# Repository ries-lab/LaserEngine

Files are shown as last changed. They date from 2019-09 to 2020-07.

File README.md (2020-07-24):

#  Open-source laser engine

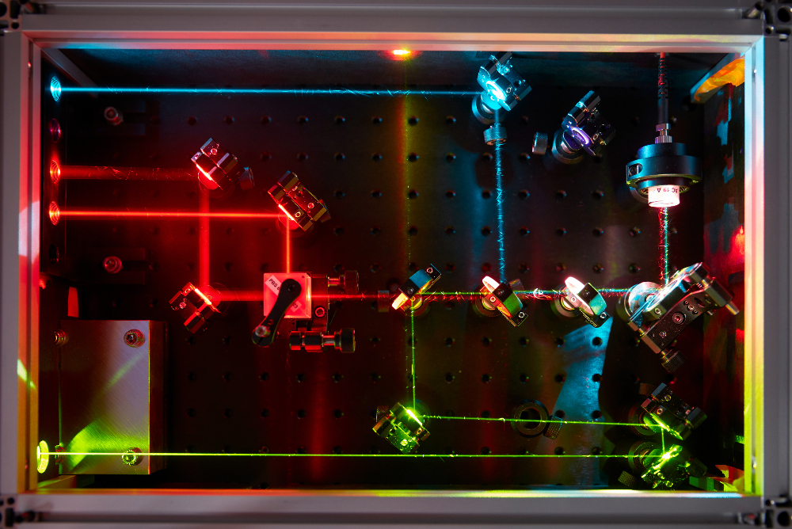
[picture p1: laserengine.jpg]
Laser engine


Blueprints for a low-cost laser engine compatible with wide-field and localization microscopy. The laser engine is based on affordable, albeit powerful, laser diodes, a square multimode fiber and a speckle-reduction module.

### :information_source: How to navigate the repository

The repository contains the following complementary modules:

- [Agitation module](Agitation_Module): a box holding a motor suspended by elastic cords for speckle and noise reduction.
- [Laser diode electronics](Electronics): Electronics to control the power and triggering of the laser diodes from the computer.
- [Laser engine](Laser_Engine): plans and guidelines of the optical path. It contains several submodules:
  - [Laser diodes mount](Laser_Engine/Diodes_Mount): A machined mount to host the TO56-canned laser diodes.
  - [Enclosure](Laser_Engine/Enclosure): A simple box to protect the laser engine from dust and the users from laser light.
  - [**(Optional)** Speckle-reduction for a 561 nm laser](Laser_Engine/LSR): In case of further speckle-reduction needed for a dpss laser, we present an optional element to place in the beam path.

### Repository updates

This repository is updated with the newest developments. If you wish to consult the repository in the state of the publication, please check out the tag **boe** within your local git copy:

```bash
git checkout boe
```

Or download the release [on Github](https://github.com/ries-lab/LaserEngine/releases/tag/boe) or [Zenodo](https://zenodo.org/badge/latestdoi/172924170).

###  :warning: Safety warnings :warning:

- Always work with adequate laser light protection.
- The foam board used in the [enclosure](Laser_Engine/Enclosure) is a fire hazard when subjected to strong laser light. Make sure to place beam stops behind the dichroic mirrors and the polarization beam splitter so that no laser beam hits the foam board panels. 
- Building the [electronics](Electronics) oneself requires experience in soldering and electronics in general. Make sure you are working safely.

#### Cite us

Daniel Schröder\*, Joran Deschamps\*, Anindita Dasgupta, Ulf Matti, and Jonas Ries, "Cost-efficient open source laser engine for microscopy," Biomed. Opt. Express 11, 609-623 (2020), [doi: 10.1364/BOE.380815](https://doi.org/10.1364/BOE.380815)

Repository on Zenodo:


#### Contact

If you have any question, get in touch with the [Ries group.](https://rieslab.de/#contact)

#### License 

[GNU LGPL](license.txt)

#### Acknowledgements

The electronics was designed by Christian Kieser, Electronics workshop, EMBL.

Pictures credit: *EMBL/Marietta Schupp*

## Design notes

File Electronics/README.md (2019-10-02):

## Electronics

To control the laser diodes, we imposed a set of constraints:

- Computer control of the **laser power** using a **[PWM](https://www.arduino.cc/en/tutorial/PWM) signal** ([Mojo FPGA](https://github.com/jdeschamps/MicroMojo) or Arduino).

- **Triggering of the laser diodes** (μs range) using a **TTL signal**.

- **Capping of the current** supplied to the laser diodes to avoid damages.

We present here two systems to drive the diodes: the electronics used in the manuscript and an alternative solution. Both are based on custom boards and commercial laser diode driver.

#### Current and voltage requirements

Note that different laser diodes have different voltage and current requirements, which complicates the task of finding a unique solution for all diodes of the laser engine:

| From the datasheets   | 405 nm, 80 mW <br />(dl-7146-301s, Sanyo) | 488 nm, 55 mW <br />(BLD-488-55, lasertack) | 640 nm, 700 mW <br />(HL63193MG, Oclaro) |
| --------------------- | ----------------------------------------- | ------------------------------------------- | ---------------------------------------- |
| Threshold current     | 60 mA                                     | 60 mA                                       | 250 mA                                   |
| Max operating current | 140 mA                                    | 135 mA                                      | 1000 mA                                  |
| Max operating voltage | 6 V                                       | 7.5 V                                       | 2.6 V                                    |

#### Solutions

We explored two solutions to control the laser diodes (we highlighted in bold each feature that is more advantageous in one version than in the other):

|                      |      [Electronics (manuscript)](Electronics_manuscript)      |     [Electronics (alternative)](Electronics_alternative)     |
| -------------------- | :----------------------------------------------------------: | :----------------------------------------------------------: |
| Status               |               **Daily use on our microscopes**               |                   Tested with a prototype                    |
| Inputs voltage       |                     3.3 V (PWM and TTL)                      |                **3.3 V or 5 V (PWM and TTL)**                |
| LD driver            | **4 x [EU-38-TTL](http://www.roithner-laser.com/ld_electronics.html) (total ~80 euros)** | 2 x [LD3000R](https://www.thorlabs.de/thorproduct.cfm?partnumber=LD3000R) + 2 x [LD1255R](https://www.thorlabs.de/thorproduct.cfm?partnumber=LD1255R) (total >600 euros) |
| Modified LD driver   |                             Yes                              |                            **No**                            |
| Power supplies       | **1 x [5 V (2.5 A)](https://www.reichelt.com/de/de/steckernetzteil-12-w-5-v-2-4-a-stabilisiert-gs15e-1p1j-p161604.html?&trstct=pos_0) + 1 x [6 V (1 A)](https://www.reichelt.com/de/en/eco-friendly-plug-in-power-supply-max-1000-ma-usb-mw-3k10gs-p87339.html?&trstct=pos_0)** | [See LD1255R power supply](https://www.thorlabs.de/newgrouppage9.cfm?objectgroup_id=1366) and <br />contact Thorlabs for the LD3000R |
| Power supplies price |                        ~ **24 euros**                        |                      prob. ~ 300 euros                       |
| Custom boards        | 4 x [signal conditioning](Electronics_manuscript/Custom_signal_conditioning) + 1 x [voltage distribution](Electronics_manuscript/Custom_voltage_distribution) |    **1 x [signal conditioning](Electronics_alternative)**    |
| LD pulsing           |                ~**40 μs (640) - 1 ms (488)**                 |                            few ms                            |

#### Notes:

- **Important**: The alternative electronics has only been tested **with a prototype**, while the manuscript version is used daily in our microscopes.
- In both cases, we generated the TTL and PWM signals using a Mojo FPGA. The FPGA firmware was based on the [MicroMojo project](https://github.com/jdeschamps/MicroMojo) and interfaced with the computer using [Micro-manager](https://micro-manager.org/). Alternatively, an Arduino can be used (also compatible with Micro-Manager).
- Each custom board was designed in [Altium](https://www.altium.com/); we uploaded here the Altium projects. Altium projects can be opened with a free license of the [Altium Designer Viewer](https://www.altium.com/altium-designer-viewer).
- The bill of materials for each custom board was exported in a format compatible with [Beta Layout](https://uk.beta-layout.com/pcb/) requirements. These can be used with the circuit PCB layout to order an already assembled board.

Both versions were designed by **Christian Kieser, Electronics workshop, EMBL**.

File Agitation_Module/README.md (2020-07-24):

## Agitation module

The agitation module consists of an aluminium box in which a motor is suspended by elastic cords. Turning on the motor causes strong vibrations in the elastics. By intertwining a multimode optical fiber in the elastics, the agitation module provides an efficient way to suppress speckles. 

#### Parts

###### Agitation box

- [Machined box parts](AgitationBox)
- [3D printed handle](AgitationBox/Handle) x1
- [Cable tie base](https://www.thorlabs.de/thorproduct.cfm?partnumber=CMS010) x4
- [2.5 mm elastic cords](https://www.prym.com/en/elastic-cord-1.5mm-black-3m-971064?c=4315) x3

###### Motor

- [Motor v1](Motors/Motor_v1) (used in the publication), which features a cheap [vibration electric motor](http://www.sourcingmap.com/dc-156v-16500rpm-vibration-electric-micro-mini-motor-140-for-massager-p-811318.html) with limited lifetime.
  or

- [Motor v2](Motors/Motor_v2) (newer version), which features a more expensive [brushless motor](https://www.amazon.de/gp/product/B07777ZH3J/ref=ox_sc_act_title_1?smid=A3TCAMEHRX2HS1&psc=1) with increased durability.

  **We advise using version v2 of the motor system.**

All non-machined or 3D-printed part references can be found in [the parts folder](Parts). Each motor version requires specific parts, described in their subfolders.

#### Guidelines

In the manuscript, we used an heavy aluminium box (30 cm thick walls):

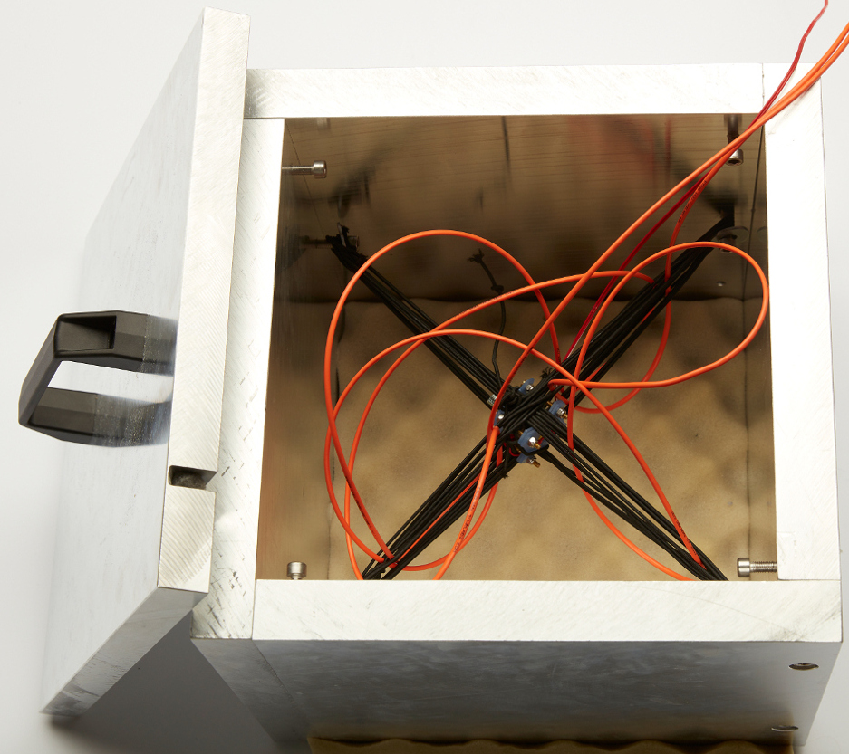
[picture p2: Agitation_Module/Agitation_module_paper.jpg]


Here, we present a lighter version:

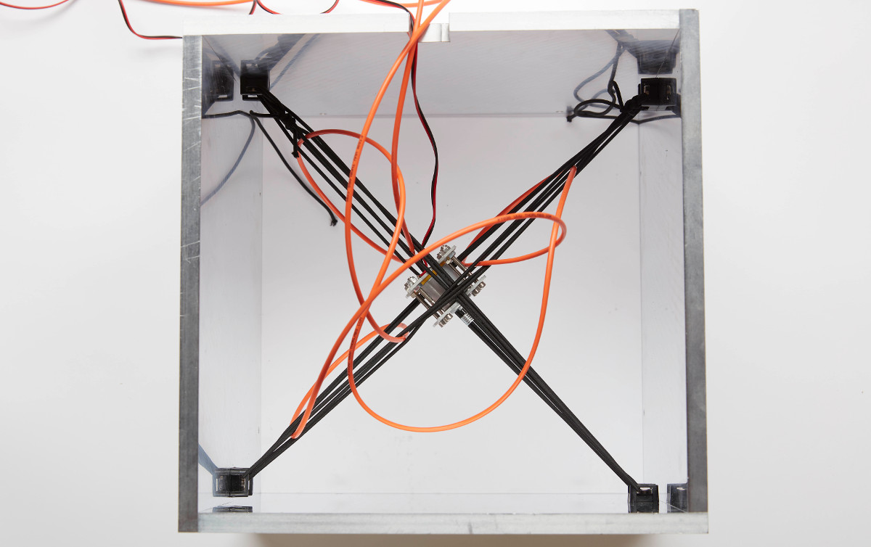
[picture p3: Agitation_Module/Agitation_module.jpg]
Agitation module


In their corresponding folders, you will find the guidelines regarding the mounting of the motor in its housing.

1. In [the box CAD folder](AgitationBox) you can find the blueprints for a lighter version of the agitation box. It consists of four panels screwed together with M4 screws. One of the panel has a dent to let the motor power supply cable and the optical fiber enter & leave the box. A lid is also described, with a [3D printed handle](AgitationBox_V2/Handle), in order to dampen the noise. The lid features four M3 screws at the corner to prevent it from sliding from the box.

   > Tip: We placed an egg box foam under the box to protect the floor and improve the noise dampening.

2. The box side panels each have an M4 thread to screw a cable tie base. The elastic cords can be tied to the handles of opposite base to create a diagonal bundle. **We advise creating a top and bottom bundles, along each diagonal, at least 5 cords strong each (as in the first picture).**

3. Mount the motor in its 3D-printed housing, either the [v1](Motors/Motor_v1) or the [v2](Motors/Motor_v2), according to its guidelines.

4. The v1 motor can simply be placed in between the elastic cord bundles, the bundles resting on a curved side of the housing (see pictures). The v2 motor can be secured to the elastic cord bundles with small cable ties going through its handles. 

5. In order to assert the efficiency of the speckle-reduction, image the optical fiber output on a camera (make sure you are focusing it properly) and turn on the motor. The speed of the motor (and therefore the supplied voltage), the tension of the cables and the mounting of the motor have an impact on the speckle-reduction efficiency.

Pictures credit: *EMBL/Marietta Schupp*

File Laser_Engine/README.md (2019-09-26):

## Laser engine optical path

The laser engine is composed of four submodules: the diode holder, the main optical path, the enclosure and the LSR system. The main optical path is described here, check the submodules for the corresponding part lists and guidelines.

#### Parts

- [405 nm laser diode (dl-7146-301s, Sanyo)](http://www.roithner-laser.com/ld_standard.html) x1

- [488 nm laser diode (BLD-488-55, Lasertack)](https://www.lasertack.com/en/55mw-488nm-laser-diode) x1

- [638 nm laser diodes (HL63193MG, Ushio)](https://www.lasershop.de/en/ushio-hl63193mg-red-laser-diode-700mw-5-6mm.html) x2

- [Diodes mount](Diodes_Mount)

- [Thorlabs part list](Parts/Thorlabs_parts_list)

- [Enclosure](Enclosure)

- [**(Optional)** 561 nm dpss laser](https://www.laserquantum.com/products/detail.cfm?id=65)

- [**(Optional)** LSR system](LSR)

#### Guidelines

The laser engine optical path is build on a breadboard, with each optical element centered on a hole to facilitate alignment:

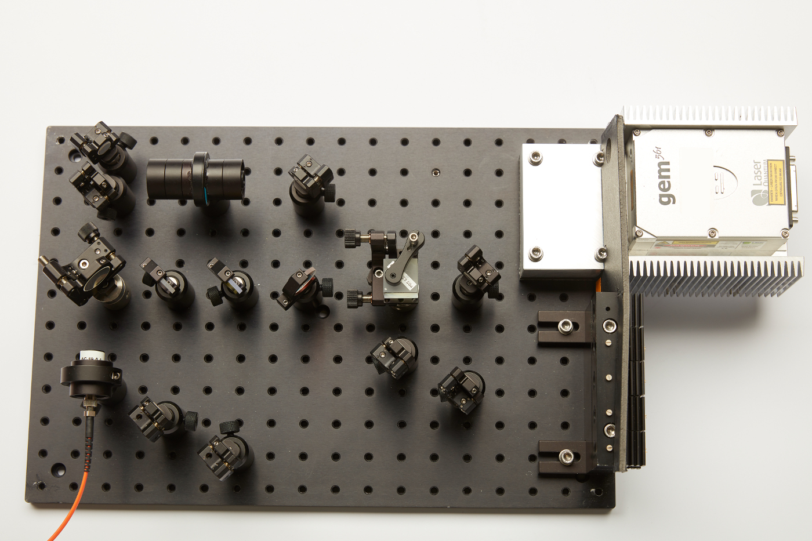
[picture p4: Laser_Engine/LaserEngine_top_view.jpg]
Optical path


The main optical path is composed of Thorlabs parts. Refer to [the following pdf](Optical_path_with_Thorlabs_parts.pdf) for the exact composition and position of each element (here in lower resolution):

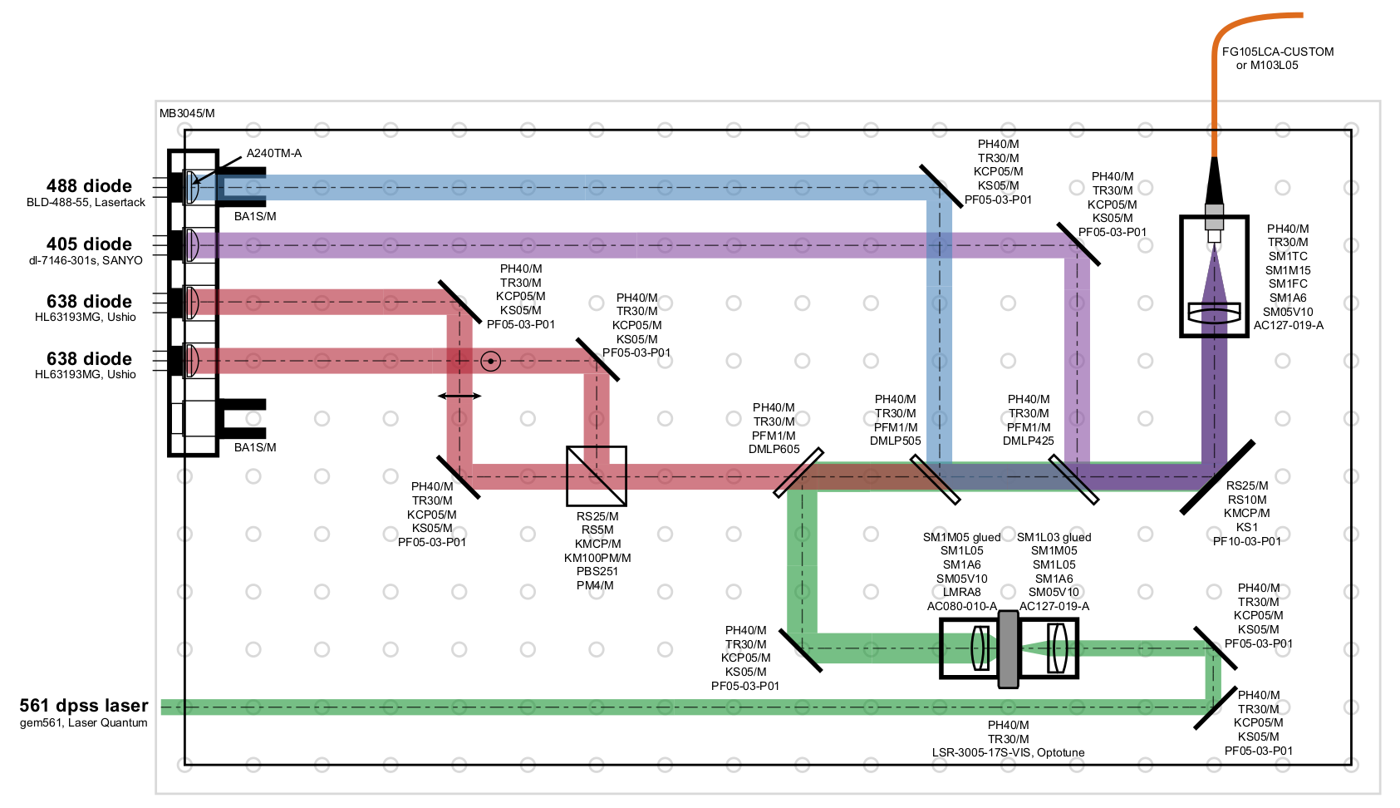
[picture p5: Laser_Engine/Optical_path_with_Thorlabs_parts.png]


Note that the LSR system is only needed if you need further speckle reduction with a dpss laser. The alignment procedure for the LSR system can be found [here](LSR). The LSR system is composed of all elements of the beam path that are exclusively on the 561 nm laser path.

> **Important**: The laser diode and dpss laser can be quite bright and will be collimated during alignment, **wear appropriate laser light protection**.

1. The first step is to mount the diodes in the holder and collimate them (see [diodes mount](Diodes_Mount)).
2. Place and fix the mount on the breadboard (use the picture above as reference for the positioning) so that the back is aligned with the edge. The collimated beams from each diode should go along the breadboard holes.
3. The easiest way to align the coupling system (multimode fiber and lens) is to couple an alignment laser from the optical fiber exit (with respect to the laser engine) and collimate the output. Place the fiber adapter plate at the extremity of the SM1M15 lens tube. The lens tube can then be held by a SM1 clamp (SM1TC) mounted on the post. Then mount the 19 mm lens in the 1/2" adjustable lens tube (SM05V10) and place the lens tube on the SM05-SM1 adapter.  At the other extremity of the SM1M15, screw the adapter with the lens residing inside the lens tube (SM1M15). You can then move the lens inward by screwing further the SM05V10 on the adapter. Once the laser light collimated, fix the SM05V10 with the locking ring.
4. Use the collimated laser coming from the optical fiber to fix the coupling system at the right height (**70 mm**) and angle (laser along the holes of the breadboard).
5. Place the reflective elements (mirrors, dichroics, beam splitter) at the positions indicated [on the optical path plan](Optical_path_with_Thorlabs_parts.pdf). Use the collimated laser to set the heights and angle (laser going along the holes).
6. Remove the alignment laser and place a power meter at the fiber exit in order to report the laser power coming out of the optical fiber. Each laser beam has two mirrors (or one mirror and one dichroic mirror) allowing to walk the beam. Start by aligning the shortest wavelength (here the 405 nm diode): first walk the beam until some laser light exits the fiber, then maximize the power coming out.
7. Repeat for the 488 nm diode. 
8. If present, align the 561 nm laser. If applicable, refer to the [laser speckle reducer](LSR) module in order to mount the LSR correctly. Coupling of the laser in the optical fiber is better achieved with the LSR turned on (as the coupling efficiency might be different with or without the LSR running).
9. The two red laser diodes are superimposed using perpendicular polarizations and a polarization beam splitter. In order to align the polarizations, place the polarization beam splitter in the right orientation (refer to the [Thorlabs page](https://www.thorlabs.de/newgrouppage9.cfm?objectgroup_id=739) for the cube orientation). Then slightly unscrew the heat sink on the first red diode. If the diode beam is the transmitted one, then rotate the diode until its profile is horizontal (you need to be above the lasing threshold). Maximize the transmitted power through the beam splitter before fixing again the diode on the mount.
10. Next, repeat the procedure with the second laser diode, with this time a perpendicular orientation of the beam profile. (If the laser beam is the reflected beam, then the profile should be oriented vertically).
11. Finally, maximize the coupling of the red diodes in the optical fiber by beam walking them. Coupling can further be improved by also rotating the square optical fiber so that the long axis of the fiber profile is aligned with the long axis of the diode profiles. 
12. Place the enclosure on top of the breadboard to protect the user and the optics. 
    **:warning: Warning: make sure to place beam stops to prevent strong laser light from hitting the foam board, as it can catch fire. :warning:**
13. The illumination on the microscope is described in the paper and might depends on the microscope itself.

We obtained the following coupling efficiencies (these might vary):

| with square optical fiber (M103L05) | Coupling efficiency |
| ----------------------------------- | :-----------------: |
| 405 nm                              |         47%         |
| 488 nm                              |         80%         |
| 638-1 nm                            |         80%         |
| 638-2 nm                            |         80%         |
| 561 nm (LSR)                        |         50%         |
| 561 nm (no LSR)                     |         81%         |

> Note that the fiber launch might also have an impact on the illumination profile and that playing with the coupling in of the laser beam can lead to a better profile (more top-hat) albeit with a lower coupling efficiency. 

Pictures credit: *EMBL/Marietta Schupp*

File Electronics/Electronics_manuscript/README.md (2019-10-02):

## Electronics (manuscript)

This section describes the electronics used in the paper. Here, the electronics is based on an inexpensive laser diode driver and was packaged in a control box.

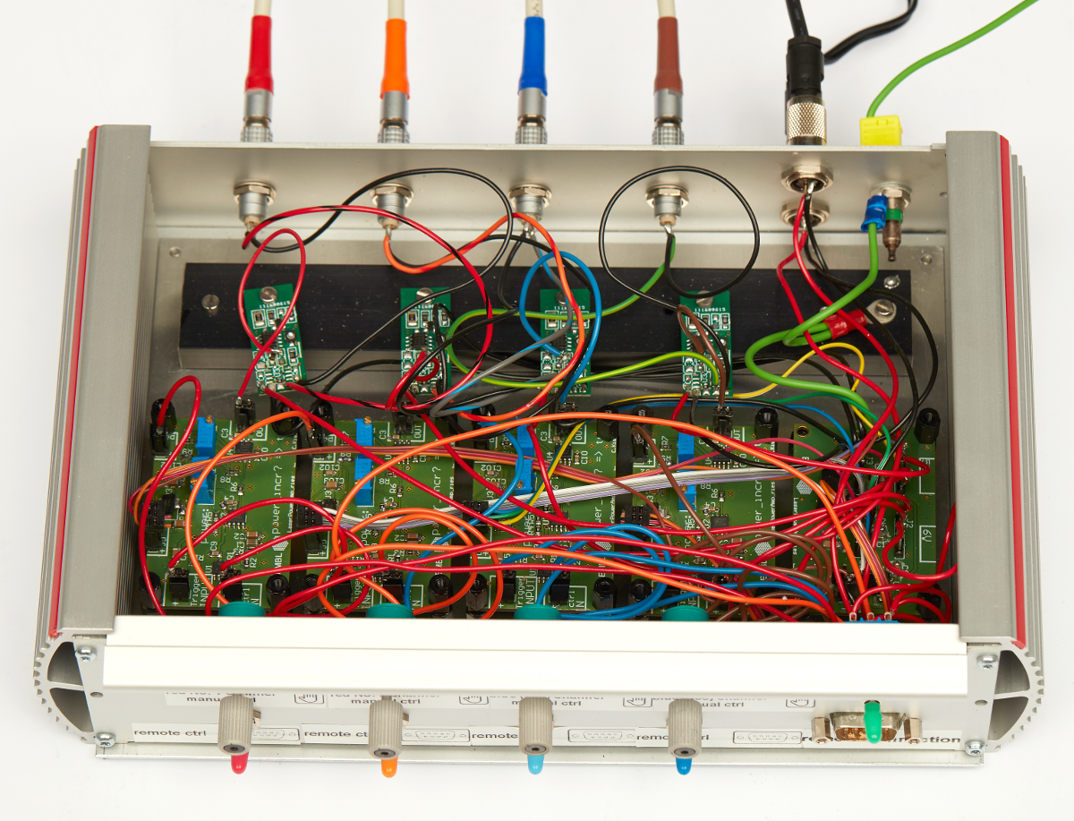
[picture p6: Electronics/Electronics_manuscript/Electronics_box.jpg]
Electronics box


The commercial **laser diode drivers** can be seen on the top row of the picture. They have been modified to bypass the board potentiometer with the output of the **signal conditioning board** (bottom row). There is one laser diode driver and one voltage conditioning board per laser diode. Finally, a **voltage distribution board** (bottom right) provides the correct voltage to each of the other elements.

The electronics has two inputs per laser diode:

- 3.3 V TTL trigger signal to switch on or off the diodes
- 3.3 V PWM (>= 1kHz) signal

**This section does not describe the boxing out of the electronics. You can find a description of the wiring involved in the [wiring](Wiring) submodule.** In particular, a feature of our electronics box is a main switch to turn on/off the laser diode and switches to allow for individual manual or remote control of the laser diodes.

#### Parts

For the four diodes described in [this section](https://github.com/ries-lab/LaserEngine/tree/master/Electronics), we need:

- [Laser diode driver](http://www.roithner-laser.com/ld_electronics.html) (eu-38-ttl, Roithner) x4

- Heat sink for the laser diode drivers (see picture above)

- [Signal conditioning board A](Custom_signal_conditioning) x2

- [Signal conditioning board B](Custom_signal_conditioning) x2

- [Voltage distribution board](Custom_voltage_distribution) x1

- [Power supply #1](https://www.reichelt.com/de/en/eco-friendly-plug-in-power-supply-max-1000-ma-usb-mw-3k10gs-p87339.html?&trstct=pos_0) (set to 6 V, 1 A)

- [Power supply #2](https://www.reichelt.com/de/de/steckernetzteil-12-w-5-v-2-4-a-stabilisiert-gs15e-1p1j-p161604.html?&trstct=pos_0) (5 V, 2.5 A)

- Controller (Arduino Due or [Mojo FPGA](https://github.com/jdeschamps/MicroMojo)) capable of delivering 3.3 V TTLs and PWMs signals 

#### Guidelines

 The guidelines describe few steps we took to build the electronics. For each laser diode, theses steps were followed independently. We advise repeating these steps in case of laser diode to laser diode variability. If you order the custom boards with the components already soldered, they you might want to verify the first steps to insure you have the correct current range output. The grounds from all boards and power supplies are connected.

> **Important**: **The laser diodes need to have proper heat dissipation otherwise they will not reach their maximum output power and will shut off, or even be irremediably damaged.** 

1. In all further steps, the voltage supply originates from the [voltage distribution board](Custom_voltage_distribution). Check the corresponding submodule for the guidelines relative to the voltage supply wiring.

   > Note: In our case, the laser diode drivers for the 405 nm and 488 nm required 5 V, while the drivers for the 638 nm laser diodes required 6 V.

2. **Connect the commercial laser diode driver to the laser diode without powering it**. Respect the anode / cathode pins. **Decrease the potentiometer to the minimum (measure the output current)**.

3. Slowly increase the laser diode output power using the potentiometer and measure the voltage between the two resistors (see picture). Measure the voltage at the maximum power output (Vmax): 

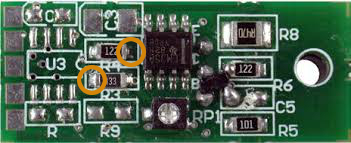
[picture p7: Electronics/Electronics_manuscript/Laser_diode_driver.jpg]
eu-38-ttl
   |  |
   | :----------------------------------: |
   | Copyright Roithner LaserTechnik GmbH |

   For instance, we obtained:

| 405 nm  | 488 nm  | 638 nm (1) | 638 nm (2) |
| ------- | ------- | ---------- | ---------- |
| 40 mV | 40 mV | 330 mV    | 330 mV    |

   Measure in addition the **maximum current** going to the laser diode.

4. Then, **[calculate](http://www.ohmslawcalculator.com/voltage-divider-calculator)** the resistors needed in the voltage divider part of the signal conversion board. As we wanted to scale the voltage from 0 - 3.3 V to 0 - Vmax. In our case, this yields two different **signal conditioning boards (A and B)** with different voltage division factors (see **[circuit](Custom_signal_conditioning/Circuit)** for the positions of the resistors R1, R2 and R3):

   |                         | A: 405 / 488 nm | B: 638 nm |
   | ----------------------- | --------------- | --------- |
   | Voltage division factor | 79              | 10        |
   | Z1 (R1 + R2)            | 68 + 10 kΩ      | 0 + 9 kΩ  |
   | Z2 (R3)                 | 1 kΩ            | 1 kΩ      |

   > Note: The voltage divider circuit is followed by an amplification and offset stages on the circuit. The choice of the voltage division dictates the range of current that can be supplied to the laser diode driver. Choosing a lower voltage after division would allow for the possibility to decrease in the future the maximum voltage supplied without exchanging the resistors.

5. **Once the resistors soldered on the signal conditioning board**, the output voltage (Out signal) range needs to be tuned using the two **potentiometers (#1 and #2, respectively R10 and R12 on the [circuit](Custom_signal_conditioning/Circuit))** present on the board. **Connect the PWM (3.3 V, we used a period of 2 ms) source to the signal conditioning board**.

6. In an iterative manner, turn potentiometer #1 (offset) so the minimum of the PWM signal corresponds to a slightly negative voltage (few mV). Then tune potentiometer #2 (gain) so that the maximum of the PWM corresponds to expected maximum output voltage. Repeat until the minimum is few mV negative and the maximum the expected value measured in step 2.

   > Note that if you did not reach the correct range, the voltage divider factor will have to be modified to increase or decrease it (by choosing different resistors).

7. The next step requires modifying the commercial laser diode driver and connecting it to the signal conditioning board. Unsolder the resistors on the laser diode driver at the points where the voltage was measured previously. **Pull the unsoldered pins away from the board and solder them together with the positive output from the signal conditioning board**.

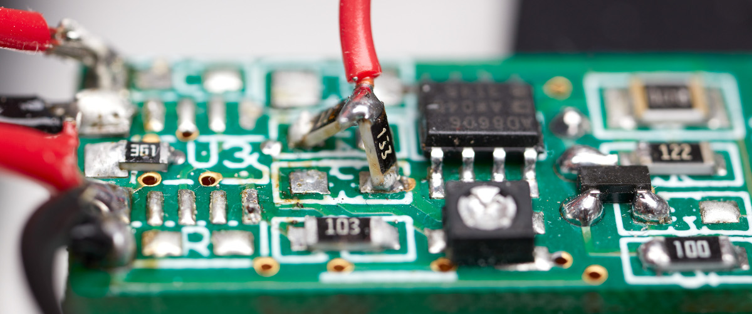
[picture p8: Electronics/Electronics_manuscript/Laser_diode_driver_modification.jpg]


   > **Note from Roithner Lasertechnik GmbH**: Any modification to the EU-38-TTL is carried out at ones own risk and responsibility. Roithner Lasertechnik GmbH has not verified and can not be held liable for any operating failure or damage resulting from the modification to the driver.

8. Before connecting back the laser diode, verify that the current output of the laser diode driver is still close to the measured current in step 2.

9. If the laser diode is still emitting at the minimum PWM value, decrease slightly potentiometer #1.

10. Repeat for the other laser diodes. Then wire the TTL inputs directly on the laser diode drivers.

#### Pulsing lag and rise-time

Using an oscilloscope, we measured the delay, the rise time and the fall time of each diode while using a TTL trigger with a pulse length of 4 ms (405 nm and 488 nm) or 400 μs (638 nm). Note that the results depend on the power set-point (separated by a "|").

| PWM 33% \| 100% |      405 nm      |     488 nm     |    638 nm (1)    |   638 nm (2)    |
| --------------- | :--------------: | :------------: | :--------------: | :-------------: |
| Delay           | 400 μs \| 400 μs | 1 ms \| 700 μs |  40 μs \| 2 μs   |  60 μs \| 5 μs  |
| Rise time       | 100 μs \| 77 μs  | 157 μs\| 67 μs |  18 μs \| 13 μs  | 15 μs \| 21 μs  |
| Fall time       |  26 μs \| 1 μs   | 15 μs \| 7 μs  | 300 μs \| 500 ns | 170 ns\| 600 ns |

#### Possible improvement

- Remove the 3.3 voltage generation in the signal conditioning boards and instead make it available through the voltage distribution board.
- Redesigned the voltage distribution board to take only the 5 V power supply and generate the 6 V voltage by itself.

Close-up picture of the modified laser diode driver credit: *EMBL/Marietta Schupp*

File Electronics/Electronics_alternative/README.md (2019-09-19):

## Electronics (alternative)

#### **Important: the electronics described here was validated using a prototype only.**

The electronics introduced in this section is an alternative to the electronics used on our microscopes and in the manuscript. It should more easily reproducible as it does not involve modifying the laser diode drivers and uses only a single custom board. However, the laser diode drivers and the power supplies are substantially more expensive. 

- **Input** (per laser diode): a TTL signal (3.3 V or 5 V) for triggering and a PWM signal (3.3 V or 5 V) for laser power control.
- **Triggering with ms pulses**.
- **Capping of the current to the laser diodes to avoid damage**.

#### Parts

For the four diodes described in [this section](https://github.com/ries-lab/LaserEngine/tree/master/Electronics).

- [High current driver LD3000R](https://www.thorlabs.de/thorproduct.cfm?partnumber=LD3000R) x2

- Power supply for the LD3000R: Note that the LD300R requires positive as well as a negative voltage power supplies. Contact Thorlabs for guidelines on choosing an appropriate power source.

- [Low current driver LD1255R](https://www.thorlabs.de/thorproduct.cfm?partnumber=LD1255R) x2

- [Power supply for the LD1255R + cable](https://www.thorlabs.de/newgrouppage9.cfm?objectgroup_id=1366) x2

- [Custom laser diode signal conversion board](Custom_signal_conditioning) x1

- Power supply for the custom board (12 V) x1

- Controller (Arduino or Mojo FPGA) capable of delivering 3.3 V or 5 V TTLs and PWMs signals. 

#### Guidelines

The laser diodes used in this project require two different current range: 60-150 mA (405 nm and 488 nm LDs) and 100-1000 mA (638 nm LDs). Therefore they are controlled here by two different LD drivers:

|                    | 405 nm & 488 nm                                              | 638 nm                                                       |
| ------------------ | ------------------------------------------------------------ | ------------------------------------------------------------ |
| Laser diode driver | [LD1255R](https://www.thorlabs.de/thorproduct.cfm?partnumber=LD1255R) | [LD3000R](https://www.thorlabs.de/thorproduct.cfm?partnumber=LD3000R) |

Each LD driver can be set to an external control mode by placing a jumper on two pins (J2). Refer to their respective data sheet and set them to external control mode.

The [custom signal conversion board](Custom_signal_conditioning) takes two inputs (3.3 V or 5 V):

- TTL trigger for on/off switching and pulsing
- PWM for power control

The board features five channels (for five laser diodes) that can be adapted to the input type and voltage. Each channel has a header:

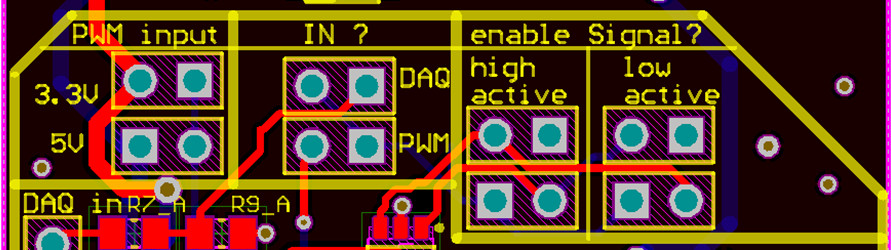
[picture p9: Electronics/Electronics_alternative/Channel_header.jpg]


Using jumpers, choose for each channel:

- 3.3 V or 5 V input
- Analog or PWM input for power control
- High or Low active for the trigger

**Important: place only a single jumper in each section (the yellow rectangles on the picture)! Note that for the high or low active, there are two sections, therefore two jumpers are necessary (top and bottom).**

The signal conversion board produces an analog signal that can be fed directly onto the external control pin of the LD drivers. **In addition, it features a potentiometer that allows decreasing the maximum voltage fed to the LD driver (< 5 V) in order to cap the current at the laser diode and prevent damages.**

Finally, make sure to correctly wire the anode and the cathode of each diode to the proper pin on the LD drivers.

> **Note**: The last segment of the circuit (see [circuit](Custom_signal_conditioning/Circuit)) holds two resistors R5 and R6 which are open and 0 Ω respectively. Therefore this part of the circuit is just a voltage follower. However, replacing R5 and R6 would allow for higher output voltage if ever necessary (e.g. 0-10V). 
>
> **Note**: We did not attempt to supply the positive and negative voltages for the LD3000R, LD1255R and the custom board using the same sources. It should be possible to reduce the number of power supply by grouping them.

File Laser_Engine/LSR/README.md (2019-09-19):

## Laser speckle-reducer assembly (optional)

The LSR system is aimed at further suppressing the laser speckles present in the output of a mutimode fiber-coupled 561 diode-pumped solid state laser. It is based on the LSR-3005-17S-VIS from Optotune, which features an oscillating membrane with diffusers. **We advise starting without this system and adding it only if the residual speckles are shown to be much stronger than those of the laser diodes.**

> Note that the LSR limits exposure times to >5 ms. 

#### Parts

Note that the Thorlabs parts used here are already present in the [Thorlabs cart corresponding to the laser engine with LSR system](https://github.com/ries-lab/LaserEngine/tree/master/Laser_Engine/Parts/Thorlabs_parts_list).

- [LSR-3005-17S-VIS, Optotune](https://www.optotune.com/products/laser-speckle-reducers/eap-lsr/lsr-3005-series) x1

- [gem561 laser](https://www.laserquantum.com/products/detail.cfm?id=65) x1

- UV glue

#### Guidelines

In order to obtain high quality speckle-reduction, the laser light must be focused on the LSR oscillating membrane and then collimated for fiber-coupling. Here, we describe the mounting and alignment of the lenses on the LSR (picture on the left).

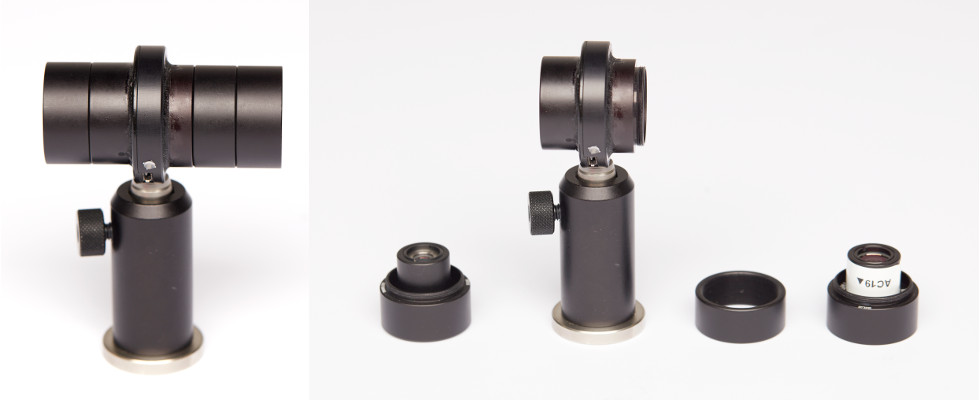
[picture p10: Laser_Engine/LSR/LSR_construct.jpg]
LSR construct


We will call the side of the LSR with prints (and a countersink hole) the "exit" and the back-side the "entrance". 

1. Make sure that the 561 nm laser is collimated before aligning the LSR system and that it propagates along the holes on the table, according to [this schematic](https://github.com/ries-lab/LaserEngine/blob/master/Laser_Engine/Optical_path_with_Thorlabs_parts.pdf).

2. Glue the 10 mm lens on its lens adapter.

3. Place each lens, the 10 mm and the 19 mm, within a SM05V10 1/2" lens tube.

4. Lock a SM1A6 1/2" to 1" adapter close to the non-threaded side of two SM1L05 lens tube.

5. Insert the SM05V10 holding the lenses each within one of the 1/2" to 1" adapter (see left-most and right-most elements on the picture on the right above). The lenses should stick out on the threaded side of the lens tubes.

6. Glue a SM1M05 on the exit side of the LSR using UV glue. Do the same with a SM1L03 on the entrance side (thread pointing outward). They should be as centered as possible, in particular with respect to each other (they should be on the same axis). See the picture above (left).

7. Screw the LSR with post and post-holder (the post holder should be a standard post holder, as opposed to the pedestal post holder on the above picture) in position in the laser engine beam path.

8. Screw a SM1M05 on the entrance side of the LSR and the element including the 19 mm lens on the same SM1M05. 

9. **With the LSR turned off**, you should see speckles in the laser bream profile after the LSR. Move the lens inward or outward in order to maximize the size of the speckles in the profile. Once you find a position with large speckles, lock the SM05V10 in place using a lock ring.

   > **Note**: The "maximum size" of the speckles is somewhat subjective, look for the larger speckles in the profile and estimate a position where they seem bigger.

10. Unscrew the entrance elements and rotate the LSR 180 degrees on its base.

11. Repeat the procedure with the 10 mm lens until you maximize the speckles size.

12. Finally, rotate again the LSR and put back the lens tube system on the entrance side . Move the laser so that the beam goes again along the holes if it has moved.

13. Place the last mirror before the dichroic (see schematic).

Pictures credit: *EMBL/Marietta Schupp*

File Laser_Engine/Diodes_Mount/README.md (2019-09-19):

## Diodes mount

The diodes mount holds all four TO56-canned laser diodes and allows for efficient heat dissipation. The mount also contain the collimating lens and can be easily fixed on the laser engine breadboard.

#### Parts

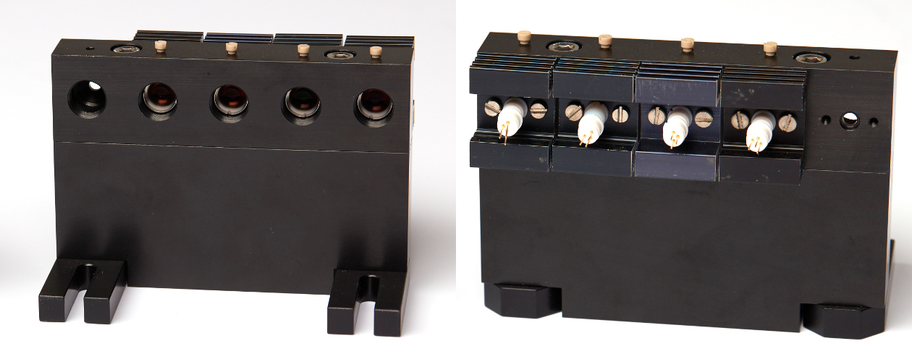
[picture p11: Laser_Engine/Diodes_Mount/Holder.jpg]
Mount


- Laser diodes (see [the main optical path section](https://github.com/ries-lab/LaserEngine/tree/master/Laser_Engine))

- [Machined mount](Machined_Mount) x1

- BA1S/M base x2

- [Heat sinks with custom holes](Heat_sinks) x4

  > **Note**: The heat sinks were produced from a longer heat sink (SK 75 75, fischer elektronik). Each heat sink was cut to be 24 mm long in order to fit more easily side by side. 25 mm long heat sinks (SK 75 25, fisher elektronik) should also work.

- Thermal paste

- [Diode sockets](https://www.buerklin.com/de/Produkte/Aktive-Bauelemente/Zubeh%C3%B6r-f%C3%BCr-Halbleiter/Halbleiterfassungen/HALBL-FASSG-TF183/p/12B190) x4

- M2 plastic screws (> 13 mm) x4

- A240TM-A aspheric lens x4

  All non-machined part references can be found in [the parts folder](Parts). **Note that the BA1S/M and the lenses are present in the [Thorlabs part list](https://github.com/ries-lab/LaserEngine/tree/master/Laser_Engine/Parts/Thorlabs_parts_list)**.

#### Guidelines

> **Note**: Laser diodes are sensitive to electrostatic discharges. If possible, use grounding when working with unmounted laser diodes.

1. Assemble the [laser diode mount](Machined_Mount) using long M6 screws. Then, with shorter ones, add the BA1S/M feet the mount base.
2. Apply a small amount of thermal paste on the sides of each laser diode (on the area where it is in contact with the mount). Then place the laser diodes in their aperture, center it and fix it by screwing on a heat sink. **Make sure that none of the laser diode pins are in contact with the heat sink to avoid shorting.** Test the diodes.
3. In order to collimate the diodes, first roughly screw the aspheric lenses in. Then turn on the diode you are collimating to a voltage above the lasing threshold (when the center linear profile starts becoming bright). **Make sure you are wearing proper laser light protections.**
4. Move the lens in or out until the laser central spot profile is not changing much during propagation over several meters. 
5. Fix the lens using the plastic screws. Avoid excessive tightening so as to not break the screw.
6. Repeat for all diodes, then move on to the laser engine alignment.

Pictures credit: *EMBL/Marietta Schupp*

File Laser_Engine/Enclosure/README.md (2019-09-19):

## Enclosure

The enclosure serves two purposes: protect the users from laser light and prevent dust from depositing on the optics. 

#### Parts

- [Aluminium profiles (25.01.####, mk)](Posts)

- [Foamboard panels (LKG55070, Boesner)](Foamboard_panels)

- [Tension fasteners](https://shop.mk-group.com/verbindungselemente/spannverbindungen/296/spannverbinder-serie-25) x8

- Tension plug (see mk catalog, 25.50.3321, mk) x4

- 3 mm M6 square nuts and 16 mm M6 maggot screws (x4)

  > **Note**: The mk 25 profiles can be bought directly from the company. An alternative to the mk 25 system is sold by [Thorlabs](https://www.thorlabs.de/newgrouppage9.cfm?objectgroup_id=194).

The components are also referenced in the [part list](Parts).

#### Guidelines

#### :warning: The foam board is sensitive to laser light and can catch fire, place beam stop to prevent string laser light from hitting the panels. :warning:

The enclosure consists of a mk 25 aluminium profile system and foamboard panels (LKG55070, Boesner) :

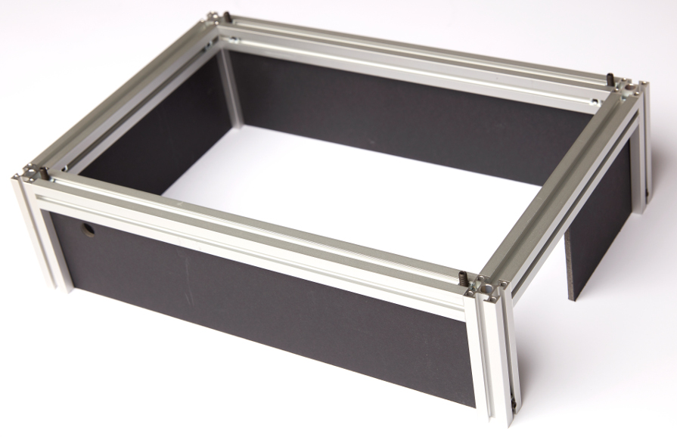
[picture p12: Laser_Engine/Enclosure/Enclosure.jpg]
Enclosure


The aluminium profiles drawing can be found in the following [folder](Posts). In order to build the enclosure, 8 MK25 aluminium profiles are necessary: 4x 120 mm long (vertical pillars), 2x 250 mm long (short side) and 2x 400 mm long (long side). 

> **Note**: All horizontal pillars have two holes on the same face to accommodate the tension fasteners (B51.03.009, mk). The fastener principle is explained in the following [catalogue](https://www.mk-group.com/fileadmin/media/catalog/en/mk_Profile_Technology_4.0.pdf), page 104. The vertical pillars have a single hole allowing locking a tension plug (25.50.3321, mk) in a similar manner.

The horizontal profiles are fixed to the vertical pillars using the tension fasteners (B51.03.009, mk). Next, we used four [foamboard panels](Foamboard_panels) inserted in the rim of the vertical pillars as side panels for the enclosure. Note that we did not draw the hole for the 561 nm laser, as this might depends on the laser itself and its mounting principle.

Four additional M6 square nuts (3 mm thick), each wtih a M6 maggot screw (16 mm long), were inserted in the top rim of the horizontal long-side pillars. The M6 screws therefore stick out of the horizontal pillar rims (see picture) and correspond to the four holes in the foamboard lid. Place the nuts correctly, then tighten the maggot screws to lock the nut in position.

Finally, we placed four mk tension plug (25.50.3321, see mk catalogue) on the laser engine breadboard corner M6 thread. The heads of the tension plugs fits in the central column of the vertical pillars and can be secured with a square nut and screw as before (see the base of the vertical pillars on the right side of the picture).

As in the picture above, the side panels have cut-out corresponding to specific elements of the laser engine: a circular hole to allow the optical fiber to enter the laser engine, a cut-out of the diode mount size and a circular hole for the 561 nm laser (optional, not drawn/represented here).  

Pictures credit: *EMBL/Marietta Schupp*

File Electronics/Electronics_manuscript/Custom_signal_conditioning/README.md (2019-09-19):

## Signal conditioning board

We produced two versions of the voltage conditioning board (A and B) with different voltage divider circuits, corresponding either the 405 nm and 488 nm (A) or the 638 nm (B)  laser diodes.

The custom board was designed using Altium (the project can be viewed with a free license of the [Altium Designer Viewer](https://www.altium.com/altium-designer-viewer)). You can find the project [here](Altium_project).

A [bill of materials](Bill_of_materials) and a [schematic of the circuit](Circuit) were automatically generated with Altium.

##### Power supply

The power is supplied to the signal conditioning board by the [custom voltage distribution board](https://github.com/ries-lab/LaserEngine/tree/master/Electronics/Electronics_manuscript/Custom_voltage_distribution): +5 V, gnd and -5 V.

##### Inputs

- 3.3 V TTL trigger signal
- 3.3 V (>=1 kHz) PWM control signal (to set the power of the laser diode)

##### Output

- Out: the Out signal should be fed directly at the intersection of the two resistors on the modified EU-38-TTL (see [previous section](https://github.com/ries-lab/LaserEngine/tree/master/Electronics/Electronics_manuscript)).
- 3.3 V voltage supply: can be used with a potentiometer to generate a manual control signal (see the [wiring](https://github.com/ries-lab/LaserEngine/tree/master/Electronics/Electronics_manuscript/Wiring) submodule for how we used a switch and a potentiometer for manual power control).

> Note: see [the wiring section](https://github.com/ries-lab/LaserEngine/tree/master/Electronics/Electronics_manuscript/Wiring) for more details on how we wired the custom boards in the electronics box.

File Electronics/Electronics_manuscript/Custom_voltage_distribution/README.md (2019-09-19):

## Voltage distribution board

The voltage distribution board simplifies the wiring within our electronics box and allows delivering negative voltage to the signal conditioning board without having a negative power supply.

#### Parts

Note that we worked with two power supplies:

- [Power supply #1](https://www.reichelt.com/de/en/eco-friendly-plug-in-power-supply-max-1000-ma-usb-mw-3k10gs-p87339.html?&trstct=pos_0) (set to 6 V, 1 A)

- [Power supply #2](https://www.reichelt.com/de/de/steckernetzteil-12-w-5-v-2-4-a-stabilisiert-gs15e-1p1j-p161604.html?&trstct=pos_0) (5 V, 2.5 A)

#### Guidelines

In order to supply voltage to the laser diode driver and to the signal conditioning board:

1. Wire the power supplies ground to the ground on the voltage distribution board.

2. Set power supply #1 voltage to 6 V. Wire its positive pin to the +6 V area of the board.

3. Wire power supply #2 positive pin to the +5 V area of the board.

   > Note: We actually soldered an interrupter between the power supplies positive pin and the voltage distribution board to be able to turn off the circuit. See the [wiring section](https://github.com/ries-lab/LaserEngine/tree/master/Electronics/Electronics_manuscript/Wiring) for more details.

4. The signal conditioning boards have 3 pins for the voltage supply: -5 V, GND and +5 V. Wire them accordingly using pins from the -5 V, ground and +5 V areas on the voltage distribution board.

5. The laser diode driver require different voltage, depending on the diodes they power. Wire the ground to the ground area, then the positive signal from the following voltage area on the board:

   | 405 nm & 488 nm | 638 nm (x2) |
   | :-------------: | :---------: |
   |      +5 V       |    +6 V     |

> Note: see [the wiring section](https://github.com/ries-lab/LaserEngine/tree/master/Electronics/Electronics_manuscript/Wiring) for more details on how we wired the custom boards in the electronics box.

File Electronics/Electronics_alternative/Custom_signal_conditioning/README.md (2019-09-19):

## Signal conditioning board

The custom board was designed using Altium (the project can be viewed with a free license of the [Altium Designer Viewer](https://www.altium.com/altium-designer-viewer)). You can find the project [here](Altium_project).

A [bill of materials](Bill_of_materials) and a [schematic of the circuit](Circuit) were automatically generated with Altium.

##### Power supply

The power is supplied to by a 12 V power supply.

##### Inputs

For each laser diode:

- 3.3 V or 5 V TTL trigger signal
- 3.3 V or 5 V (>=1 kHz) PWM control signal (to set the power of the laser diode)

##### Output

For each laser diode:

- Out: the Out signal should be fed directly to the external input of the Thorlabs laser diode driver.

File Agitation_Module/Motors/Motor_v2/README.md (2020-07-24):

## Brushless motor - v2

The brushless motor is housed in a 3D printed holder. 

#### Parts

- [KEESIN RC 1000KV Brushless Motor A2212](https://www.amazon.de/gp/product/B07BS7DFW3) x1

- [3D printed motor housing](Motor_Housing_v2) x1

- [Servo controller for speed control](https://www.amazon.de/gp/product/B07K6D9ZDQ/ref=ox_sc_act_title_1?smid=A1SPOY0RBPE5BD&psc=1) x1

- 6 mm long M3 screws x4

- 2.6 mm thick M5 hex jam nut x1

- 8 mm (inner) - 24 mm (outer) diameters extra thick fender washer x1

- 6 mm (inner) - 18 mm (outer) diameters fender washer x1

- [MR105 Ball bearing (5x10x4 mm)](https://www.kugellager-express.de/miniature-deep-groove-ball-bearing-mr105-2rs-5x10x4-mm) x1
  or
  [MR115 Ball bearing (5x11x4 mm)]( https://www.kugellager-express.de/miniature-deep-groove-ball-bearing-mr115-2rs-5x11x4-mm ) x1
  (make sure to use the correct motor housing)

- 12 V (0.5 A) power supply

  Definition of mechanical elements according to [this page](https://www.albanycountyfasteners.com/Fastener-Varieties-s/1130.htm).

#### Guidelines

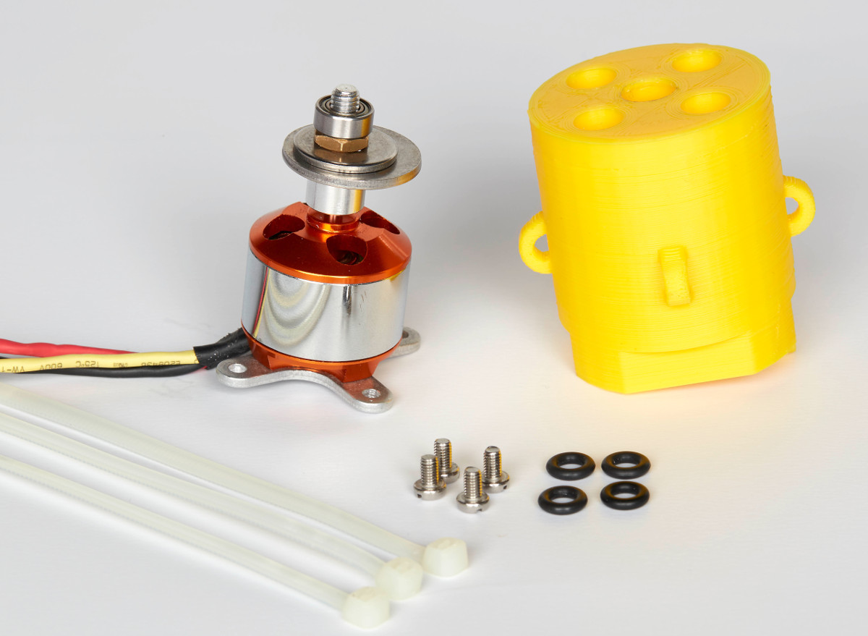
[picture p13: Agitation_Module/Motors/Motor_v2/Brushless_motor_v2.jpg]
Brushless motor and its housing


2. Fix the cross holder on the back of the motor using the screws shipped with the motor.

3. Place the [collet prop adapter](https://robu.in/product/aa212-motor-prop-adapater-collet-type/) on the [motor shaft](https://en.wikipedia.org/wiki/Shaft_(mechanical_engineering)) without the bullet tip adapter (see picture above). Add the large [fender washer](https://www.bokers.com/fender_washers.asp) then the smaller one onto the prop adapter thread. Finally screw in the M5 nut so that the fender washers are fixed non-concentrically (see how the washers are not centered on the picture) and that the prop adapter is securely clamped on the motor shaft (thanks to the [collet](https://en.wikipedia.org/wiki/Collet)). **It is important that the center of gravity of the fender washers is not on the shaft axis to produce strong agitation.**

4. Add the ball bearing to the prop adapter thread.

5. Insert the motor in the 3D housing so that the ball bearing fits in the central stepped hole.

6. Screw the motor on the housing with the M3 screws.

8. In order to power the brushless motor, you can for instance solder extensions on the wires of the motor and insert them in an adapter (here WR-TBL Serie 3405, Würth). Similarly, cut the cables on the controller and insert the bare ends in the complementary adapter (here WR-TBL Serie 3485, Würth). **Make sure to respect the correct cable connection.** Finally, solder the power and ground cables on the other side to the 12 V power supply (0.5 A). You can use the [servo controller](https://www.amazon.de/gp/product/B07K6D9ZDQ/ref=ox_sc_act_title_1?smid=A1SPOY0RBPE5BD&psc=1) to provide the speed signal. Note that in this case the servo controller gets its power from the motor controller, and the motor is powered directly from the power supply.

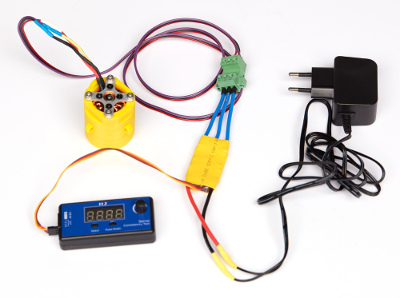
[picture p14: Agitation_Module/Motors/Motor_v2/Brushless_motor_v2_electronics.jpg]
Electronics
   

Pictures credit: *EMBL/Marietta Schupp*

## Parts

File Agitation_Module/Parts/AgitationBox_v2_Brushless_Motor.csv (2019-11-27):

Item | Serial | Company | Price (eur, 25/01/19) | Link (25/01/19)
Agitation motor | B07BS7DFW3 | Amazon | 18.99 | https://www.amazon.de/gp/product/B07BS7DFW3
Motor speed controller | B07K6D9ZDQ | Amazon | 10.99 | https://www.amazon.de/gp/product/B07K6D9ZDQ

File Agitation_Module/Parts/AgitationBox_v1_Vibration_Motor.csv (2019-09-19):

Item | Serial | Company | Price (eur, 25/01/19) | Link (25/01/19)
Agitation motor | a15112300ux0142 | Sourcingmap | 3.64 | http://www.sourcingmap.com/dc-156v-16500rpm-vibration-electric-micro-mini-motor-140-for-massager-p-811318.html

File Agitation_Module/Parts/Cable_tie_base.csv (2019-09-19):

Item | Serial | Company | Price (eur, 25/01/19) | Link (25/01/19)
Cable tie base | 233-663 | RS Components |  | https://de.rs-online.com/web/p/kabelbindermontage/0233663/
Alternative cable tie base | CMS010 | Thorlabs | https://www.thorlabs.de/thorproduct.cfm?partnumber=CMS010

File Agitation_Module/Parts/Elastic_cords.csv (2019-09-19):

Item | Serial | Company | Price (eur, 25/01/19) | Link (25/01/19)
Elastic cord | 19712310 | Prym | 2.49 | https://www.prym.com/en/elastic-cord-1.5mm-black-3m-971064?c=4315

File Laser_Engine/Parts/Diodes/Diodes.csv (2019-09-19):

Item | Serial | Company | Price (eur, 25/01/19) | Link (25/01/19)
405 nm laser diode | dl-7146-301s | SANYO | 44.4 | http://www.roithner-laser.com/ld_standard.html
488 nm laser diode | BLD-488-55 | Lasertack | 117.81 | https://www.lasertack.com/en/55mw-488nm-laser-diode
638 nm laser diode | HL63193MG | Ushio | 62 | https://www.lasershop.de/en/ushio-hl63193mg-red-laser-diode-700mw-5-6mm.html

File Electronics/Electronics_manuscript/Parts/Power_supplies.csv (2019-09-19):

Item | Serial | Company | Price (eur, 25/01/19) | Link (25/01/19)
Power supply #1 | MW 3K10GS | reichelt | 8.5 | https://www.reichelt.com/de/en/eco-friendly-plug-in-power-supply-max-1000-ma-usb-mw-3k10gs-p87339.html?trstct=pos_0
Power supply #2 | GS15E-1P1J | reichelt | 15.1 | https://www.reichelt.com/de/de/steckernetzteil-12-w-5-v-2-4-a-stabilisiert-gs15e-1p1j-p161604.html?trstct=pos_0

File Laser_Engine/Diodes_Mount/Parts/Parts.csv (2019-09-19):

Item | Serial | Company | Price (eur, 25/01/19) | Link (25/01/19)
Thermal paste | B0087X728K | Amazon | 7.19 | https://www.amazon.de/gp/product/B0087X728K/ref=ox_sc_act_title_1?smid=A3R7GTCT3A4NLT&psc=1
Socket | HALBL.FASSG.TF183 | fischer elektronik | 3.5 | https://www.buerklin.com/de/Produkte/Aktive-Bauelemente/Zubeh%C3%B6r-f%C3%BCr-Halbleiter/Halbleiterfassungen/HALBL-FASSG-TF183/p/12B190
Heatsinks | SK 75 75 | fischer elektronik |  | https://www.fischerelektronik.de/web_fischer/en_GB/heatsinks/A04/Extruded%20heatsinks%20for%20PCB%20mounting/$catalogue/fischerData/PR/SK75_75_/index.xhtml

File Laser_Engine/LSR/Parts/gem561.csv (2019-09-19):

Item | Serial | Company | Price (eur, 25/01/19) | Link (25/01/19)
561 nm laser | gem561 | LaserQuantum |  | https://www.laserquantum.com/products/detail.cfm?id=65

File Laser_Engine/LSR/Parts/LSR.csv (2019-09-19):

Item | Serial | Company | Price (eur, 25/01/19) | Link (25/01/19)
Laser speckle-reducer | LSR-3005-17S-VIS | Optotune | 635 | https://www.edmundoptics.com/f/Optotune-Laser-Speckle-Reducers/14335/

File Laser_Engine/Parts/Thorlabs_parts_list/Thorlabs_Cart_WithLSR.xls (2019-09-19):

Part Number | Item | Product URL | Qty | Price | Subtotal | Currency
MB3045/M | Aluminum Breadboard 300 mm x 450 mm x 12.7 mm M6 Taps | https://www.thorlabs.de/newgrouppage9.cfm?objectgroup_id=159 | 1 | 170.89 | 170.89 | Euro
SS6MS12 | M6 x 1.0 Stainless Steel Setscrew 12 mm Long Pack of 25 | https://www.thorlabs.de/newgrouppage9.cfm?objectgroup_id=1437 | 1 | 5.39 | 5.39 | Euro
TR30/M-P5 | Ø12.7 mm Optical Post SS M4 Setscrew M6 Tap L = 30 mm 5 Pack | https://www.thorlabs.de/newgrouppage9.cfm?objectgroup_id=1266 | 3 | 19.39 | 58.17 | Euro
PH40/M-P5 | Ø12.7 mm Post Holder Spring-Loaded Hex-Locking Thumbscrew L=40 mm 5 Pack | https://www.thorlabs.de/newgrouppage9.cfm?objectgroup_id=1268 | 3 | 32.81 | 98.43 | Euro
KCP05/M | Centering Plate for Kinematic Mirror Mount for Ø1/2" Optic Metric | https://www.thorlabs.de/newgrouppage9.cfm?objectgroup_id=3965 | 8 | 14.74 | 117.92 | Euro
KS05/M | Ø12.7 mm Precision Kinematic Mirror Mount 3 Adjusters M4 Taps | https://www.thorlabs.de/newgrouppage9.cfm?objectgroup_id=3 | 8 | 66.99 | 535.92 | Euro
PF05-03-P01 | Ø1/2" Protected Silver Mirror | https://www.thorlabs.de/newgrouppage9.cfm?objectgroup_id=903 | 8 | 28.97 | 231.76 | Euro
PF10-03-P01 | Ø1" Protected Silver Mirror | https://www.thorlabs.de/newgrouppage9.cfm?objectgroup_id=903 | 1 | 47.29 | 47.29 | Euro
PBS251 | 1" Polarizing Beamsplitter Cube 420 - 680 nm | https://www.thorlabs.de/newgrouppage9.cfm?objectgroup_id=739 | 1 | 202.13 | 202.13 | Euro
RS25/M | Ø25.0 mm Pillar Post M6 Taps L = 25 mm M4 Adapter Included | https://www.thorlabs.de/newgrouppage9.cfm?objectgroup_id=241 | 2 | 17.52 | 35.04 | Euro
RS5M | Ø25 mm Post Spacer Thickness = 5 mm | https://www.thorlabs.de/newgrouppage9.cfm?objectgroup_id=851 | 1 | 7.21 | 7.21 | Euro
RS10M | Ø25 mm Post Spacer Thickness = 10 mm | https://www.thorlabs.de/newgrouppage9.cfm?objectgroup_id=851 | 1 | 7.83 | 7.83 | Euro
KMCP/M | Kinematic Mount Centering Plate Metric | https://www.thorlabs.de/newgrouppage9.cfm?objectgroup_id=3965 | 2 | 18.54 | 37.08 | Euro
KM100PM/M | Kinematic Prism Mount 25.4 mm Deep M4 Taps | https://www.thorlabs.de/newgrouppage9.cfm?objectgroup_id=1811 | 1 | 68.61 | 68.61 | Euro
PM4/M | Large Adjustable Clamping Arm M4 Threaded Post | https://www.thorlabs.de/newgrouppage9.cfm?objectgroup_id=2546 | 1 | 20.86 | 20.86 | Euro
KS1 | Ø1" Precision Kinematic Mirror Mount 3 Adjusters | https://www.thorlabs.de/newgrouppage9.cfm?objectgroup_id=3 | 1 | 79.27 | 79.27 | Euro
PFM1/M | 120° Clear-Edge Flexure Mount for Ø1" (Ø25.4 mm) Optics M4 Tapped Hole | https://www.thorlabs.de/newgrouppage9.cfm?objectgroup_id=8797 | 3 | 34.12 | 102.36 | Euro
DMLP425 | Ø1&quot; Longpass Dichroic Mirror 425 nm Cutoff | https://www.thorlabs.de/newgrouppage9.cfm?objectgroup_id=3313 | 1 | 156.69 | 156.69 | Euro
DMLP505 | Ø1&quot; Longpass Dichroic Mirror 505 nm Cutoff | https://www.thorlabs.de/newgrouppage9.cfm?objectgroup_id=3313 | 1 | 156.69 | 156.69 | Euro
DMLP605 | Ø1&quot; Longpass Dichroic Mirror 605 nm Cutoff | https://www.thorlabs.de/newgrouppage9.cfm?objectgroup_id=3313 | 1 | 156.69 | 156.69 | Euro
A240TM-A | f = 8.00 mm NA = 0.5 Mounted Rochester Aspheric Lens AR: 350 - 700 nm | https://www.thorlabs.de/newgrouppage9.cfm?objectgroup_id=3810 | 4 | 77.19 | 308.76 | Euro
M103L05 | Square-Core Fiber Patch Cable 150 µm x 150 µm Core FC/PC 5 m | https://www.thorlabs.com/newgrouppage9.cfm?objectgroup_id=10638 | 1 | 106.73 | 106.73 | Euro
SM1FC | FC/PC Fiber Adapter Plate with External SM1 (1.035"-40) Thread | https://www.thorlabs.de/newgrouppage9.cfm?objectgroup_id=69 | 1 | 26.89 | 26.89 | Euro
AC127-019-A | f=19.0 mm Ø1/2" Achromatic Doublet ARC: 400-700 nm | https://www.thorlabs.de/newgrouppage9.cfm?objectgroup_id=120 | 2 | 47.29 | 94.58 | Euro
SM1A6 | Adapter with External SM1 Threads and Internal SM05 Threads 0.15" Thick | https://www.thorlabs.de/newgrouppage9.cfm?objectgroup_id=1524 | 3 | 17.8 | 53.4 | Euro
SM05V10 | Ø1/2" Adjustable Lens Tube 0.8" Travel | https://www.thorlabs.de/newgrouppage9.cfm?objectgroup_id=3310 | 3 | 30.68 | 92.04 | Euro
SM1M15 | SM1 Lens Tube Without External Threads 1.5" Long Two Retaining Rings Included | https://www.thorlabs.de/newgrouppage9.cfm?objectgroup_id=3307 | 1 | 15.19 | 15.19 | Euro
SM1TC | Ø1.20" Clamp for SM1 Lens Tubes and C-Mount Extension Tubes | https://www.thorlabs.de/newgrouppage9.cfm?objectgroup_id=1533 | 1 | 39.17 | 39.17 | Euro
AC080-010-A | f=10.0 mm Ø8 mm Achromatic Doublet ARC: 400-700 nm | https://www.thorlabs.de/newgrouppage9.cfm?objectgroup_id=120 | 1 | 42.88 | 42.88 | Euro
LMRA8 | LMR05 Adapter for Ø8.0 mm Optics | https://www.thorlabs.de/newgrouppage9.cfm?objectgroup_id=1433 | 1 | 14.19 | 14.19 | Euro
SM1L05 | SM1 Lens Tube 0.50" Thread Depth One Retaining Ring Included | https://www.thorlabs.de/newgrouppage9.cfm?objectgroup_id=3307 | 2 | 11.44 | 22.88 | Euro
SM1L03 | SM1 Lens Tube 0.30" Thread Depth One Retaining Ring Included | https://www.thorlabs.de/newgrouppage9.cfm?objectgroup_id=3307 | 1 | 11.05 | 11.05 | Euro
SM1M05 | SM1 Lens Tube Without External Threads 1/2" Long Two Retaining Rings Included | https://www.thorlabs.de/newgrouppage9.cfm?objectgroup_id=3307 | 2 | 11.4 | 22.8 | Euro
BA1S/M | Mounting Base 25 mm x 58 mm x 10 mm | https://www.thorlabs.de/newgrouppage9.cfm?objectgroup_id=47 | 2 | 4.73 | 9.46 | Euro

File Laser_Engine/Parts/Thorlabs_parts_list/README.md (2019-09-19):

## Thorlabs optical parts

In this folder, you can find three different files:

- [Thorlabs_Comments_on_items](Thorlabs_Comments_on_items.csv): a list of all optical elements for the main and LSR optical paths, with the quantity used (with and without LSR) and comments describing where is the item used in the optical path.
- [Thorlabs_Cart_WithoutLSR](Thorlabs_Cart_WithoutLSR.xls): a Thorlabs cart that can be directly uploaded to the website for ordering. This cart **does not include** the elements necessary to build the LSR system.
- [Thorlabs_Cart_WithLSR.xls](Thorlabs_Cart_WithLSR.xls): a Thorlabs cart that can be directly uploaded to the website for ordering. This cart **includes** the elements necessary to build the LSR system.

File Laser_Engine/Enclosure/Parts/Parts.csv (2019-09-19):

Item | Serial | Company | Price (eur, 25/01/19) | Link (25/01/19)
Aluminium profile | 25.01.0000 | mk |  | https://shop.mk-group.com/aluprofile/serie-25/1/profil-mk-2025.01?c=5
Tension fasteners | B51.03.009 | mk |  | https://shop.mk-group.com/verbindungselemente/spannverbindungen/296/spannverbinder-serie-25
Tension plug | 25.50.3321 | mk |  | see catalogue
Foam board | LKG55070 | boesner | 88 | https://www.boesner.com/rahmen/rahmen/einrahmung-und-zubehoer/kapa-graph-leichtstoffplatte#30744

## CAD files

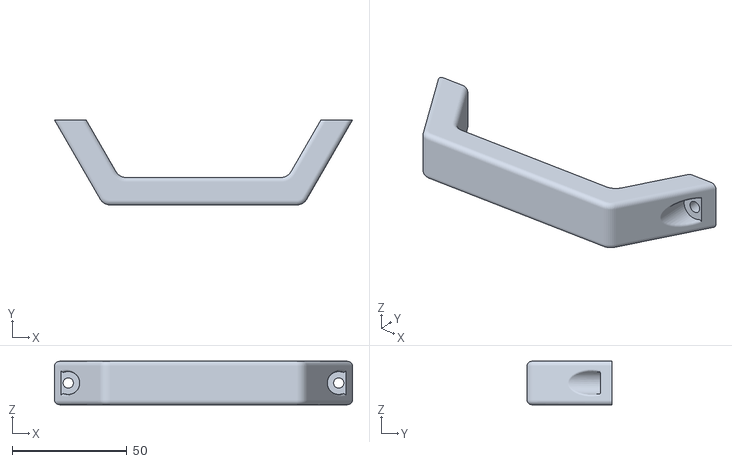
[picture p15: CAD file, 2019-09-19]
Agitation_Module/AgitationBox/Handle/HANDLE.STL
130.0 x 37.0 x 19.0

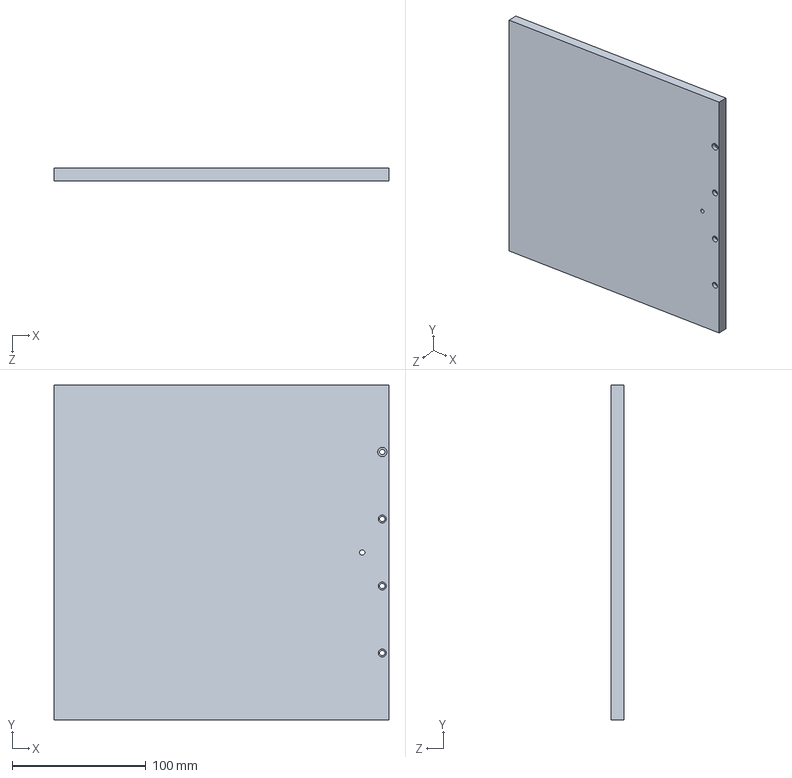
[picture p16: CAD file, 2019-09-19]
Agitation_Module/AgitationBox/SidePanel_V2.STEP
250.0 x 250.0 x 10.0 mm

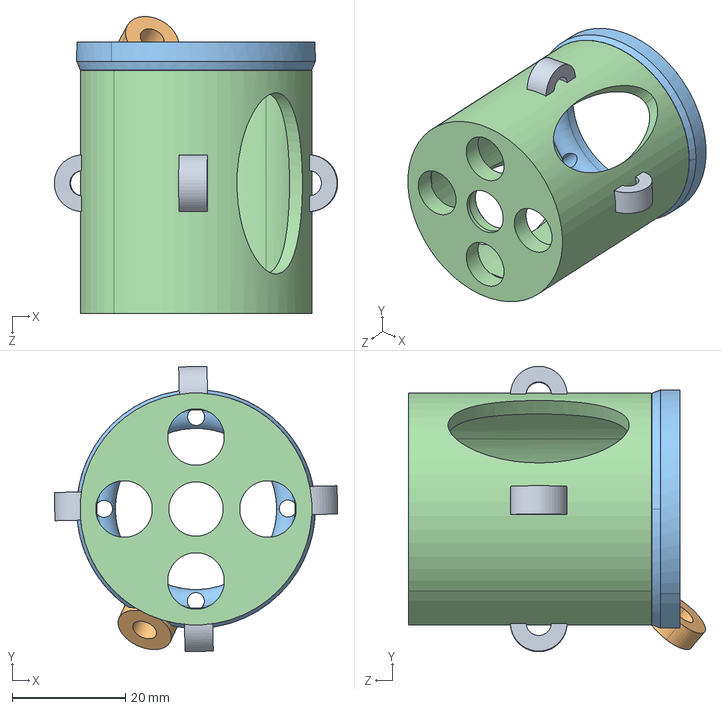
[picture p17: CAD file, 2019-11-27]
Agitation_Module/Motors/Motor_v2/Motor_Housing_v2/Agitation_motor_housing_v2_10mmBearing.STEP
50.1 x 50.5 x 52.5 mm

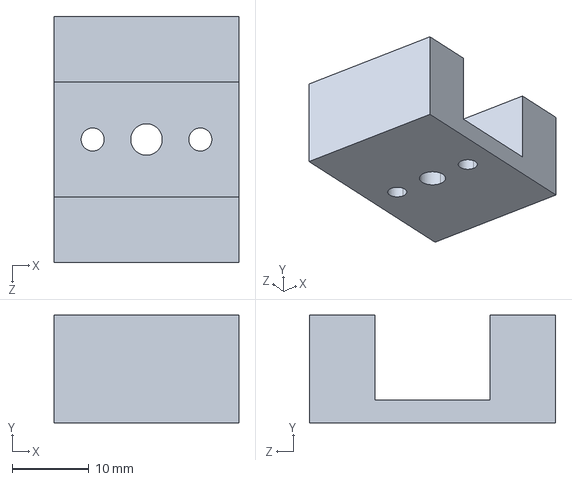
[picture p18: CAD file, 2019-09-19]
Laser_Engine/Diodes_Mount/Heat_sinks/Heatsink_holes.STEP
24.0 x 14.0 x 32.0 mm

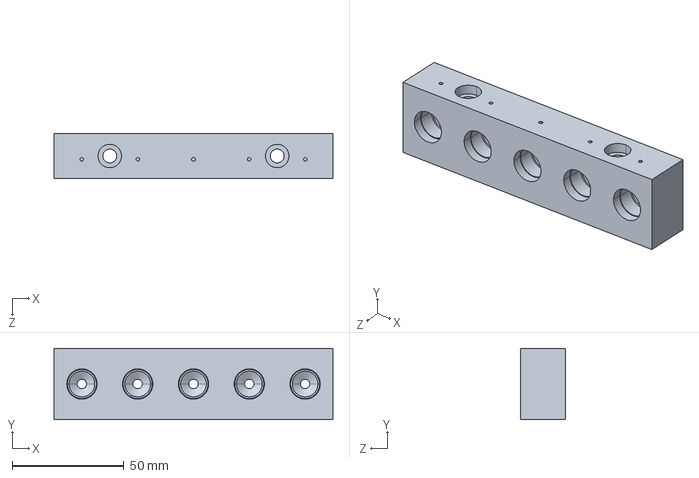
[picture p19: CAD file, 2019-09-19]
Laser_Engine/Diodes_Mount/Machined_Mount/DiodesMount_v06.STEP
125.0 x 32.0 x 20.0 mm

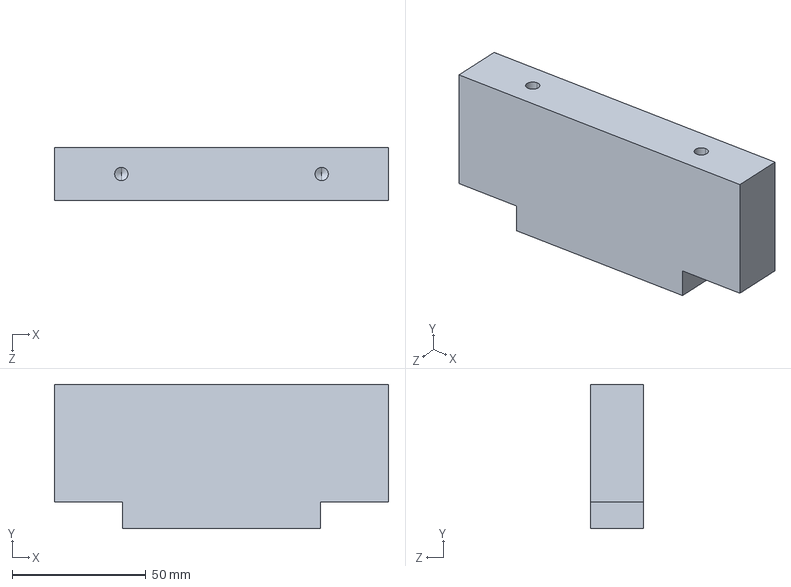
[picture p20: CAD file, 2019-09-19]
Laser_Engine/Diodes_Mount/Machined_Mount/DiodesMount_post_v06.STEP
125.0 x 54.0 x 20.0 mm

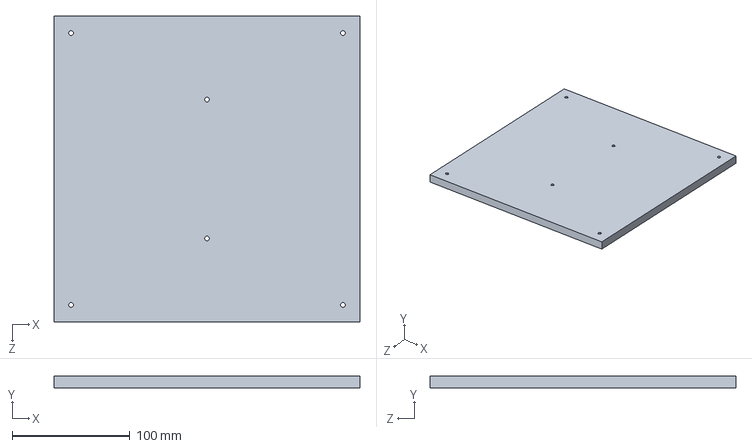
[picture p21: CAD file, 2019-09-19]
Agitation_Module/AgitationBox/Lid_V2.STEP
260.0 x 10.0 x 260.0 mm

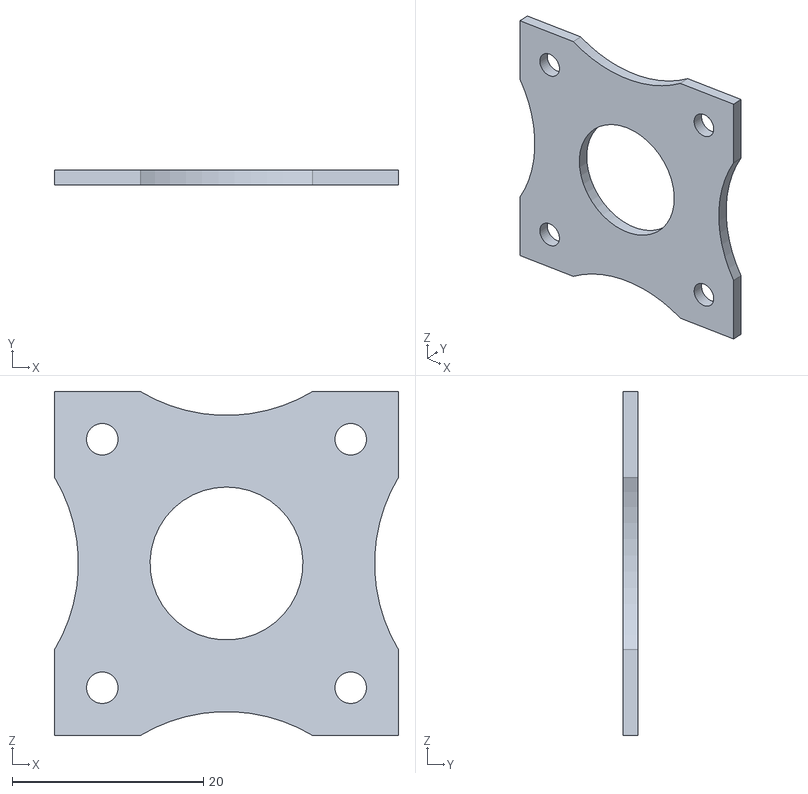
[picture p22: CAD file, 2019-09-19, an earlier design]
Agitation_Module/Motors/Motor_v1/Motor_Housing_v1/Motor_holder_v1.STL
36.0 x 1.60 x 36.0

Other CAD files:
Agitation_Module/AgitationBox/SidePanel_with_dent_V2.STEP
Agitation_Module/Motors/Motor_v2/Motor_Housing_v2/Agitation_motor_housing_v2_11mmBearing.STEP
Agitation_Module/Motors/Motor_v2/Motor_Housing_v2/Agitation_motor_housing_v2_10mmBearing.STL
Agitation_Module/Motors/Motor_v2/Motor_Housing_v2/Agitation_motor_housing_v2_11mmBearing.STL

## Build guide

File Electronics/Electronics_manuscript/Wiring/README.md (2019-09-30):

## Wiring

We packaged our electronics in a compact aluminium box (as seen in the picture [in the previous section](https://github.com/ries-lab/LaserEngine/tree/master/Electronics/Electronics_manuscript)).

Our electronics box displays a main switch allowing to interrupt the connection between the power supplies and the voltage distribution board. In addition, for each diode we added a switch between manual and remote control, as well as a potentiometer to control the laser diode power in manual mode. The laser diodes are then connected to the electronics box using a custom cable. Here are the front and back of the electronics box:

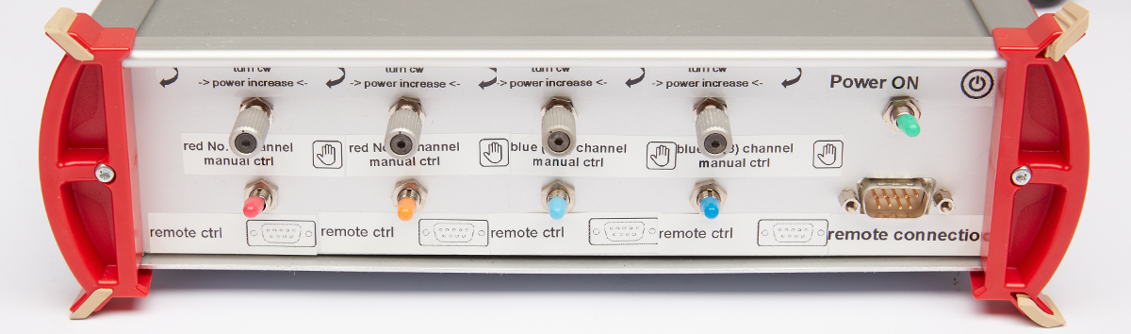
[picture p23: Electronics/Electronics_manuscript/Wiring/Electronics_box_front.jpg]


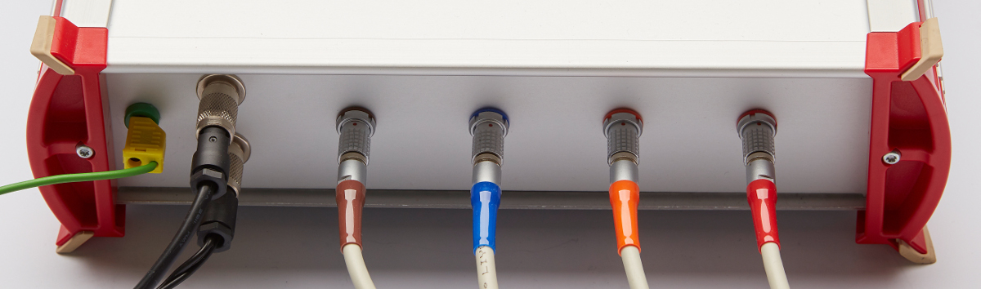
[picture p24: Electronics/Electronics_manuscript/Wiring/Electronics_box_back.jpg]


The wiring within [the electronics box](wiring.pdf) is described in the pdf file:

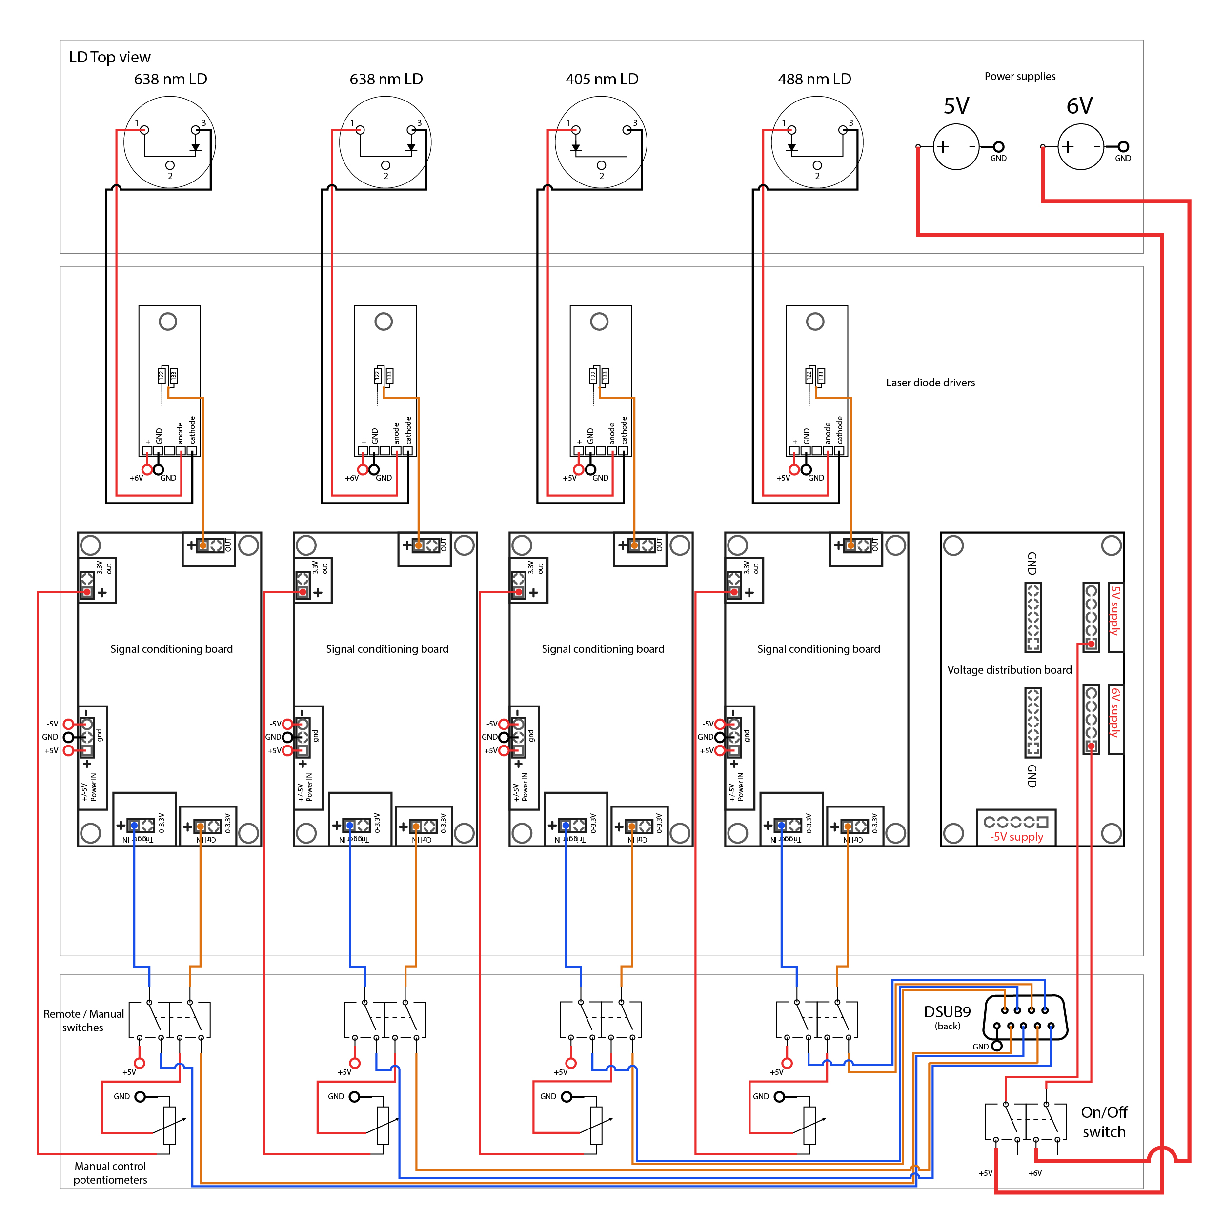
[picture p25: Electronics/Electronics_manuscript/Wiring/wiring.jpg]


#### Parts

In addition to the laser diodes, laser diode drivers, voltage conditioning boards, the voltage distribution board and the power supplies (which are described in the other submodules). 

- Aluminium enclosure (~22 x 15 cm)
- Double pole double throw switch x5
- Potentiometer x4
- DSUB9 plug: connected to 4 x TTL and 4 x PWM signals

> **Important**: You need to ground the aluminium box with the circuit and its surroundings (see green wire on the picture).

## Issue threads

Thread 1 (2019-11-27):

### ISSUE TITLE
issue with the stl file for the 3D printed motor housing

### ISSUE THREAD

**Issue by bamouroux** [ries-lab/LaserEngine#1]
Hello,
Thank you for this nice description on how to build such an agitation box =)
However I am facing an issue with the stl file for the 3D printed motor housing (for mortor v2):
It appears that the file has to be repaired before being able to print it.
I can do it with software such as Autodesk or Blender. But when I open the stl file with such a software it changes the scale of the object... 51m of length O:
Is it possible to provide an other repaired file, or just to give the length of the object (in inches or meters) so I can repair it on my own and rescale it?
Thank you in advance

**Comment by jdeschamps** [comment]
Hi!
I also see this with SolidWorks. Basically the software interprets the unit as meters, instead of mm. So you need to scale it down by 1000.

Now, we use Cura to 3D print and in this software the piece is shown at 52*50*50 mm (values from the top of my head, I don't have access to the computer now). Which software reports "file to be repaired" error? Or is this just related to the wrong unit?

Next week I can try to play around with this.

**Comment by bamouroux** [comment]
Hi !
Ok I will rescale it.
Concerning the issue, when I opened it in a fablab (I don't know which software), the object appears as an overlap of different elements which are not unified together. It seems that there are a lot of "vacuum defect" where there are changes of shape or thickness. As a result the fablab facility refused to print it, claming that this is not a stable object.

**Comment by jdeschamps** [comment]
Hi! 
Without their software I can't really test what is wrong, since we manage to print it fine on our 3D printer... Next time you pass by there, maybe you can inquire on the software they use?

Nonetheless, I just added a .3mf file in the same folder. Using solidworks, this file seems to not have the scaling problem observed earlier.

Let me know if things work out for you.

**Comment by bamouroux** [comment]
Hi!
Sorry for my late answer, I was waiting for the last component (long delay to get delivered the rolling ball) to assemble the box with the new version of the housing motor's file you provide.
Regarding to the new file you provide I found good points and sources of improvements.
At first, this new file solves the main problems I found with the first one.
- the new file does not show lot of errors. It could be solved by the software used at the fablab (sorry I forgot to ask the name of it).
- the scaling issue is fixed, the object is directly 50.9x50.9x52 if I remember.
However I faced 2 major issues:
     -The middle hole for the rolling ball is just too small to allow it to go in. Therefore the housing motor is not long enough. I think an idea should be to increase the diameter of this hole from 0.5 cm that will allow the user to place it more easily. If it move a little it is not a big deal.
     -The 4 holes for the M3 screws are too big (3cm vs 2.5cm diameter for M3 screws)
 A final suggestion should be to provide the file to print the housing motor in ".stl" format which is the one mainly used by 3D printed software, or to advice a free software able to convert ".3mf" to the ".stl" format.

**Comment by jdeschamps** [comment]
Thanks for the feedback!

>   -The middle hole for the rolling ball is just too small to allow it to go in. Therefore the housing motor is not long enough. I think an idea should be to increase the diameter of this hole from 0.5 cm that will allow the user to place it more easily. If it move a little it is not a big deal.

Actually that's by design, the person who designed it wanted it tight. So we usually hammer it in. :)
Maybe I should add a note in the description.

>   -The 4 holes for the M3 screws are too big (3cm vs 2.5cm diameter for M3 screws)

On the 3mf files I measure 3 mm holes, as well as on our 3D printed left overs. Where did you observe the 2.5 mm ? On the file or on your printed piece?

As far as I know we did not have problems screwing in small M3 screws in those holes on different pieces.

>   A final suggestion should be to provide the file to print the housing motor in ".stl" format which is the one mainly used by 3D printed software, or to advice a free software able to convert ".3mf" to the ".stl" format.

I agree, unfortunately if I export the .3mf with Solidworks to .stl, then I end up again with the problem you observed: a 50 m tall model...  I will try with another software.

Unfortunately it was designed as meshes directly, I would have a CAD file things would be easier to scale/modify/export.

**Comment by bamouroux** [comment]
Thank you for your answers, I will answer to the points you mentionned:
-Ok, I like the hammer solution =). I was scared to do it ^^
-I observed the 2.5mm holes on the final printed piece. I don't know why as I did not modified your file, just converted it to .stl with a software found online (nchsoftware - convert 3D  meshes).
-For the scaling I think it is no a big problem. Knowing the real dimensions of you object is enough to rescale it (in 1s) at any 3D-printing facility. 
Based on your model, I designed a similar object with "Autodesk Inventor" and I face the same scaling issue.

**Comment by jdeschamps** [comment]
Interestingly enough, it turns out STL files do not contain any scale information. So the fault resides in the software that imports them ([source wikipedia](https://en.wikipedia.org/wiki/STL_(file_format)#cite_note-7)).

I updated the designs with a better version, including this time the STEP files. So that anyone can export the STL files from them!

I consider this issue closed, let me know if you feel differently. :)

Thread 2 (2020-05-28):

### ISSUE TITLE
Use >5V power supply for agitator

### ISSUE THREAD

**Issue by ptbrown1729** [ries-lab/LaserEngine#2]
A comment (not an issue) which I hope will be helpful to others, since I spent some time troubleshooting when building the agitator module myself.

The electronic speed controller board is power by a 5V regulator, so using a 5V DC power supply may not be sufficient for the regulators to operate properly. A 9V power supply will work fine.

Using the 5V power supply caused me some confusion because the regulator only output 4V, which was enough to power the servo consistency tester but not the ERC.

Thanks for making this design available!

**Comment by dschr** [comment]
Thank you for mentioning this, it is a good point and true indeed. In a new iteration of the engine, we use a 15V input with a different, but similar motor. However, it now needs an active cooling system, which we wanted and still want to leave out. So, I plan to test at some point a more expensive, yet efficient motor.

**Comment by jdeschamps** [comment]
Actually there is a mistake indeed in the current guide (Motor V2). We actually are using a 12 V and not a 5 V power supply. 

Thanks for catching this @ptbrown1729 ! Let us know if the update to the motor V2 guide now makes sense and we can close the issue.

**Comment by jdeschamps** [comment]
I consider it closed!

best

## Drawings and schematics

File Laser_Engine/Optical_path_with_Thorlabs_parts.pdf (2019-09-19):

## 488 diode

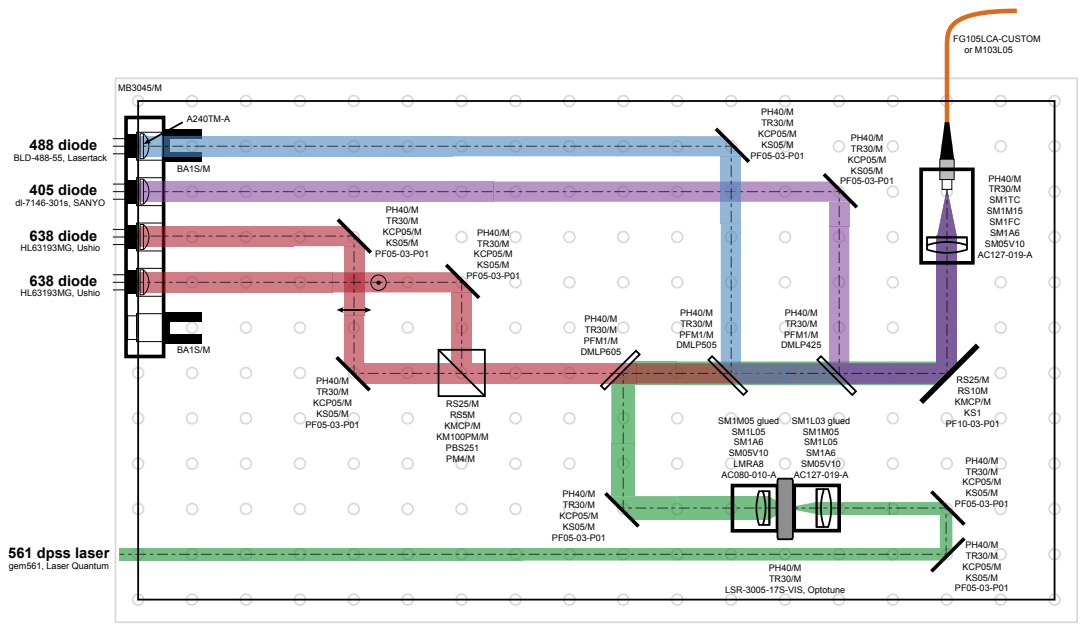
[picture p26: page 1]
638 diode; 561 dpss laser; 405 diode; BLD-488-55, Lasertack; dl-7146-301s, SANYO; HL63193MG, Ushio; gem561, Laser Quantum; RS25/M RS5M KMCP/M KM100PM/M PBS251 PM4/M; PH40/M TR30/M KCP05/M KS05/M PF05-03-P01; PH40/M TR30/M PFM1/M DMLP605; PH40/M TR30/M PFM1/M DMLP505; PH40/M TR30/M PFM1/M DMLP425; RS25/M RS10M KMCP/M KS1 PF10-03-P01; FG105LCA-CUSTOM or M103L05; SM1L03 glued SM1M05 SM1L05 SM1A6 SM05V10 AC127-019-A; SM1M05 glued SM1L05 SM1A6 SM05V10 LMRA8 AC080-010-A

LSR-3005-17S-VIS, Optotune

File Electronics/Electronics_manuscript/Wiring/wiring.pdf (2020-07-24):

+ - | + -

## 638 nm LD

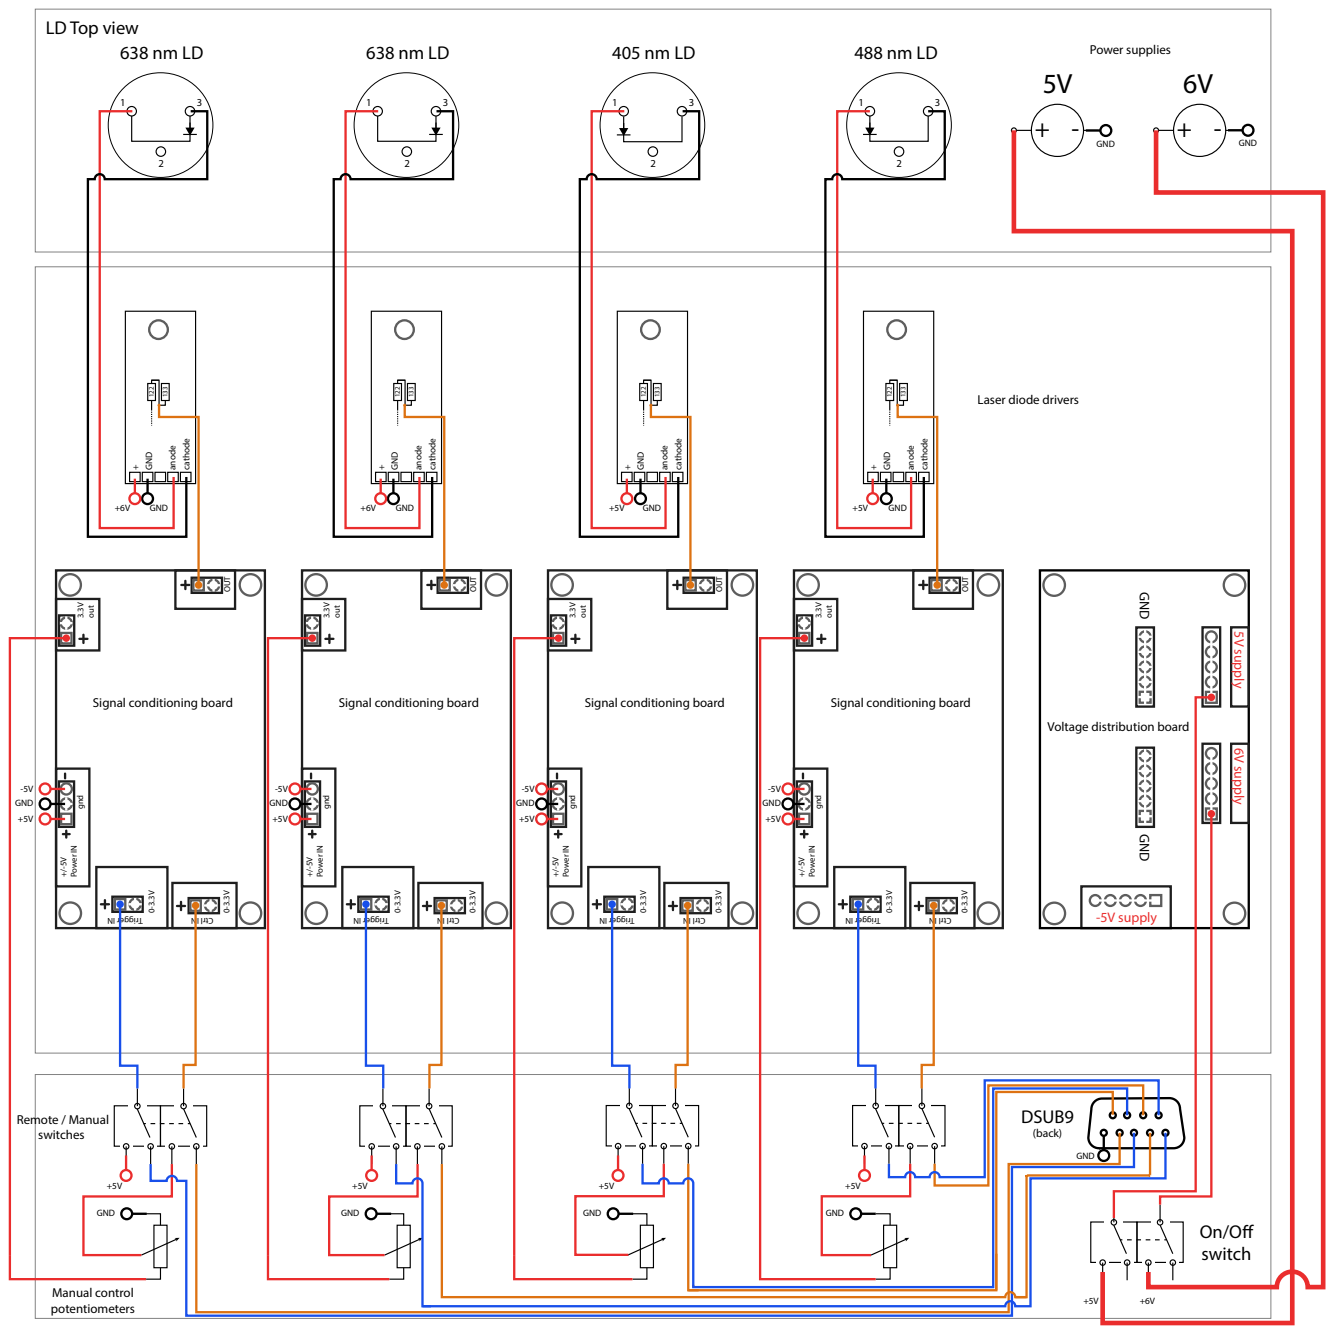
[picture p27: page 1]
DSUB9 (back); On/O switch; Power IN; gnd 3.3V out; 0-3.3V OUT; GND; anode; cathode; 5V supply 6V supply; Power supplies; Remote / Manual switches; Manual control potentiometers; GND +5V

LD Top view

Laser diode drivers

0-3.3V OUT
-5V supply GND GND

Signal conditioning board

Voltage distribution board

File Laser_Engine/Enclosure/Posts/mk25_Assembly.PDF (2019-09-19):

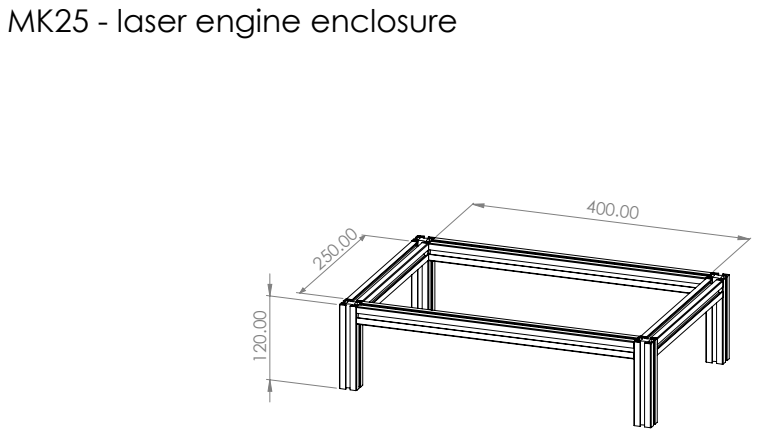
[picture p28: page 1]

MK25 - laser engine enclosure

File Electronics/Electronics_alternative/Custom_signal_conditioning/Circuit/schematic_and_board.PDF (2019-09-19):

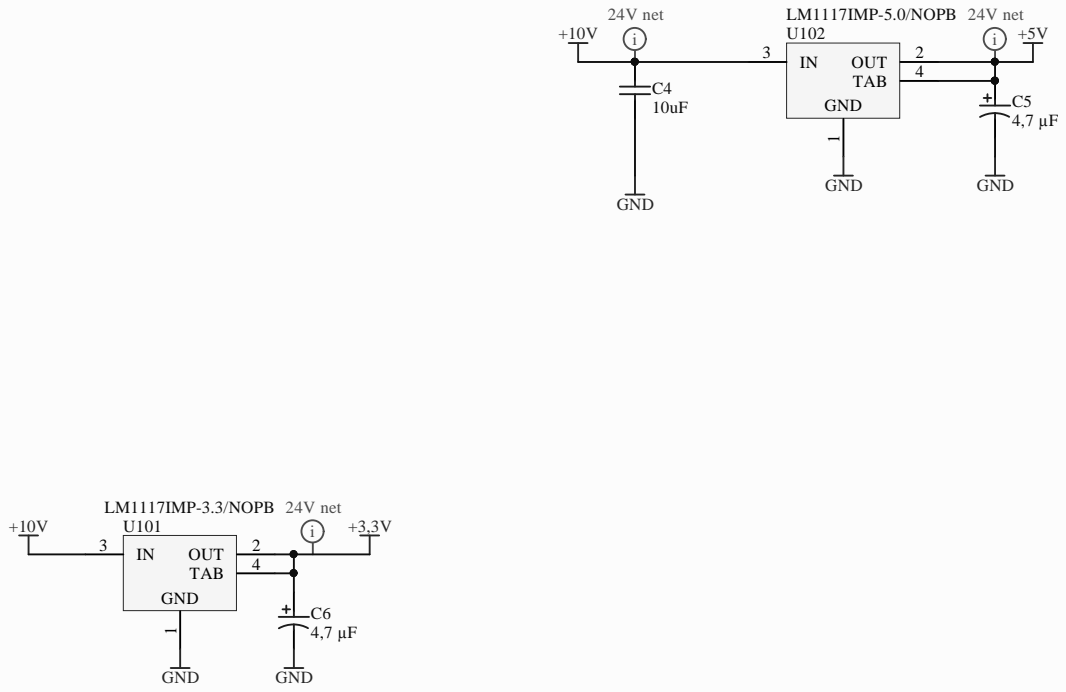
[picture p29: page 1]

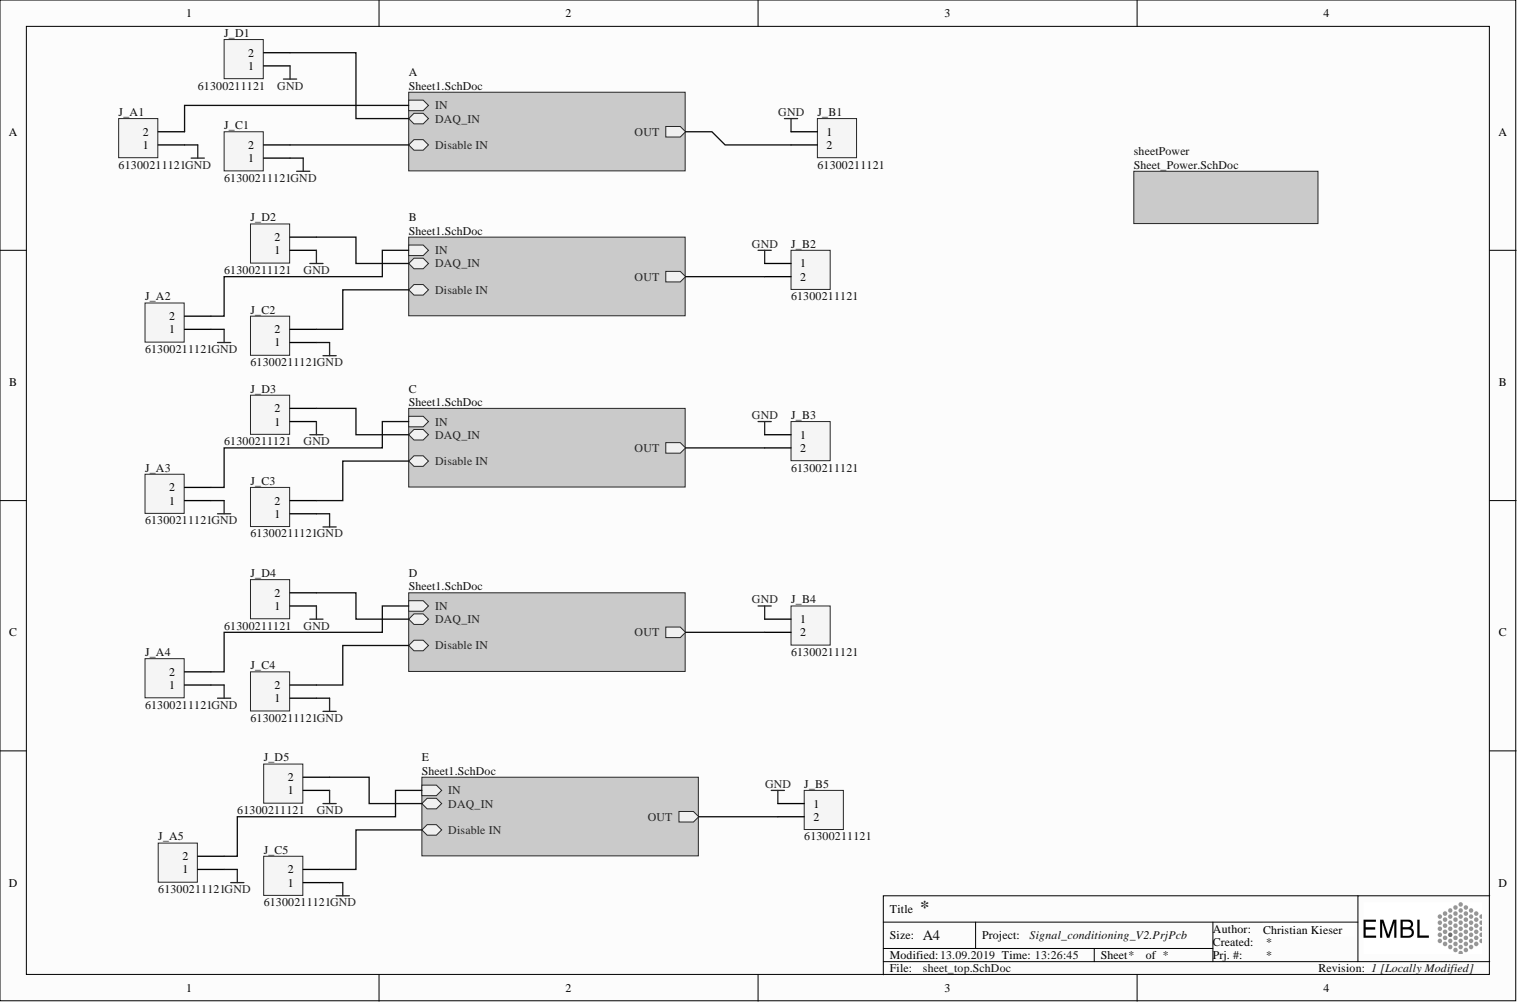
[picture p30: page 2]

J_C1

Title *

Size: A4 | Project: | Created: Prj. #: | Christian Kieser Alfons Riedinger * Signal_conditioning_V2.PrjPcb

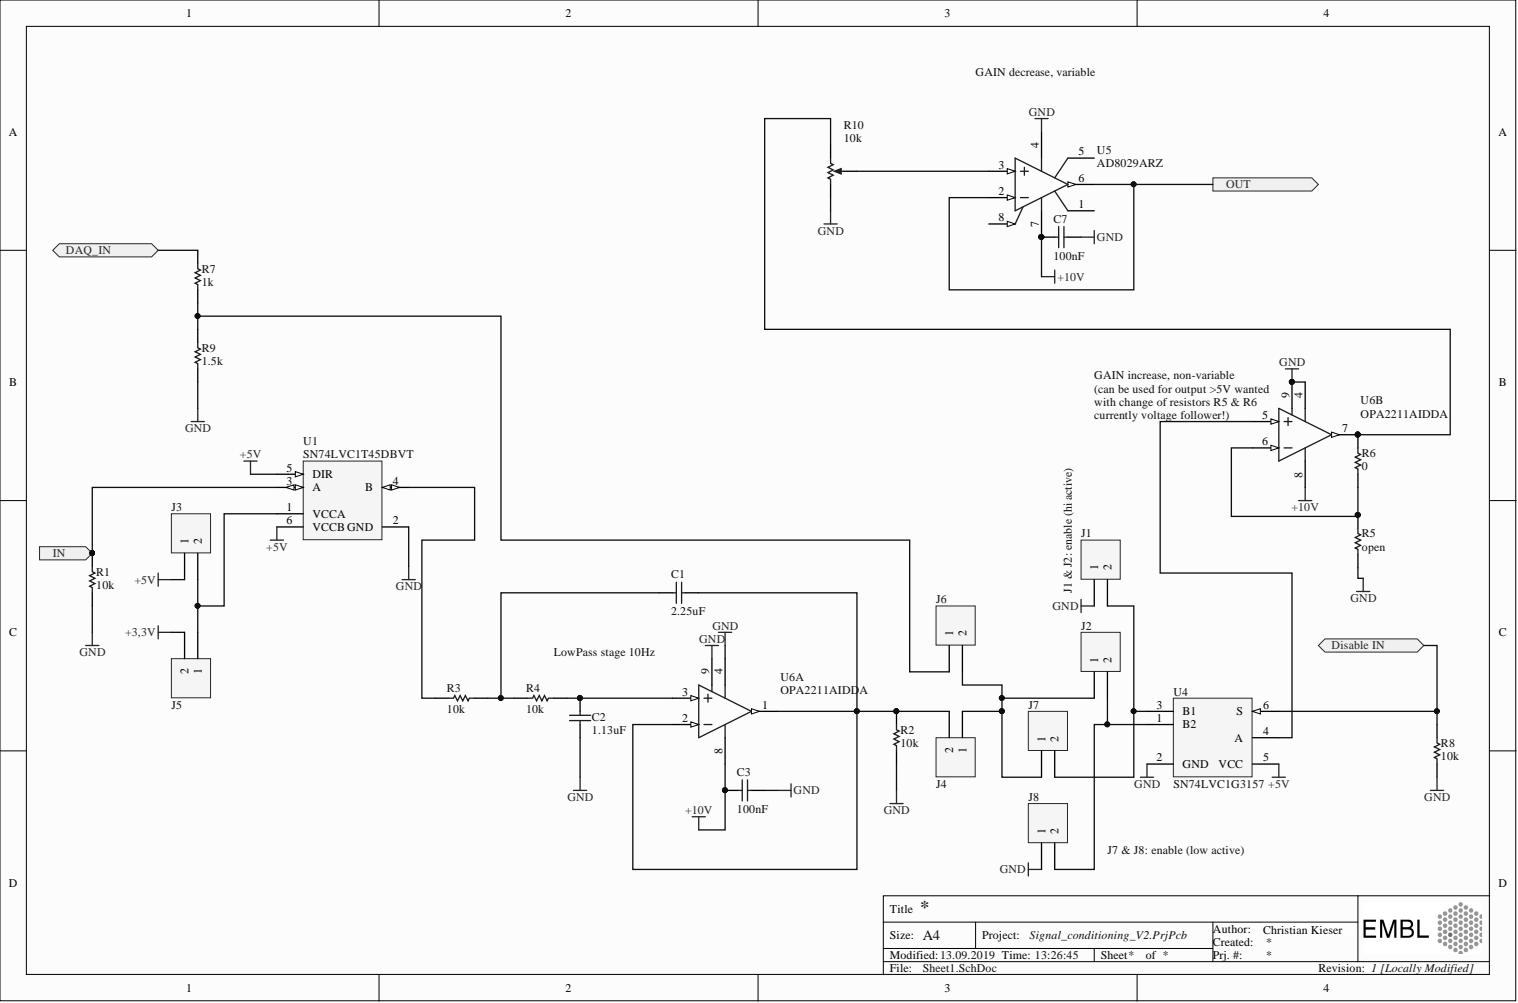
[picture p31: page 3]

Size: A | Project : S i g n a l _co n d i t i o n i n g _ V2.P rj Pcb | Created : Prj. # : | Chri A lfo s n t s R ian K ied ieser i n ger

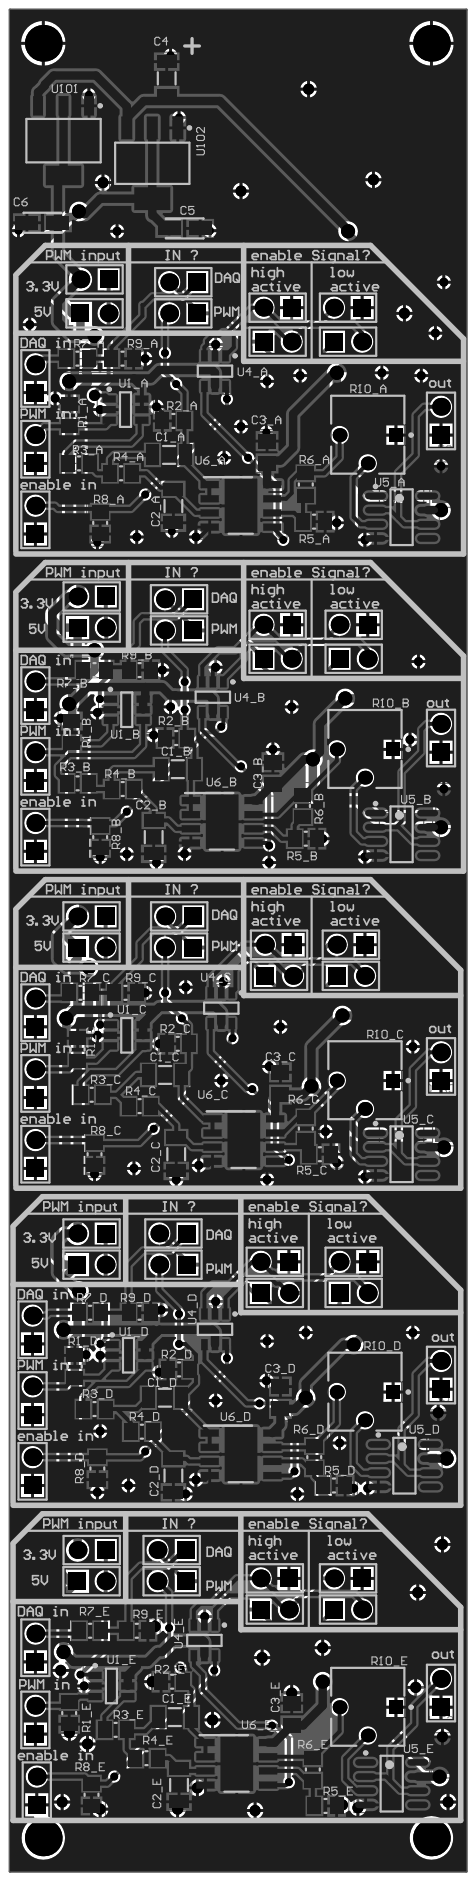
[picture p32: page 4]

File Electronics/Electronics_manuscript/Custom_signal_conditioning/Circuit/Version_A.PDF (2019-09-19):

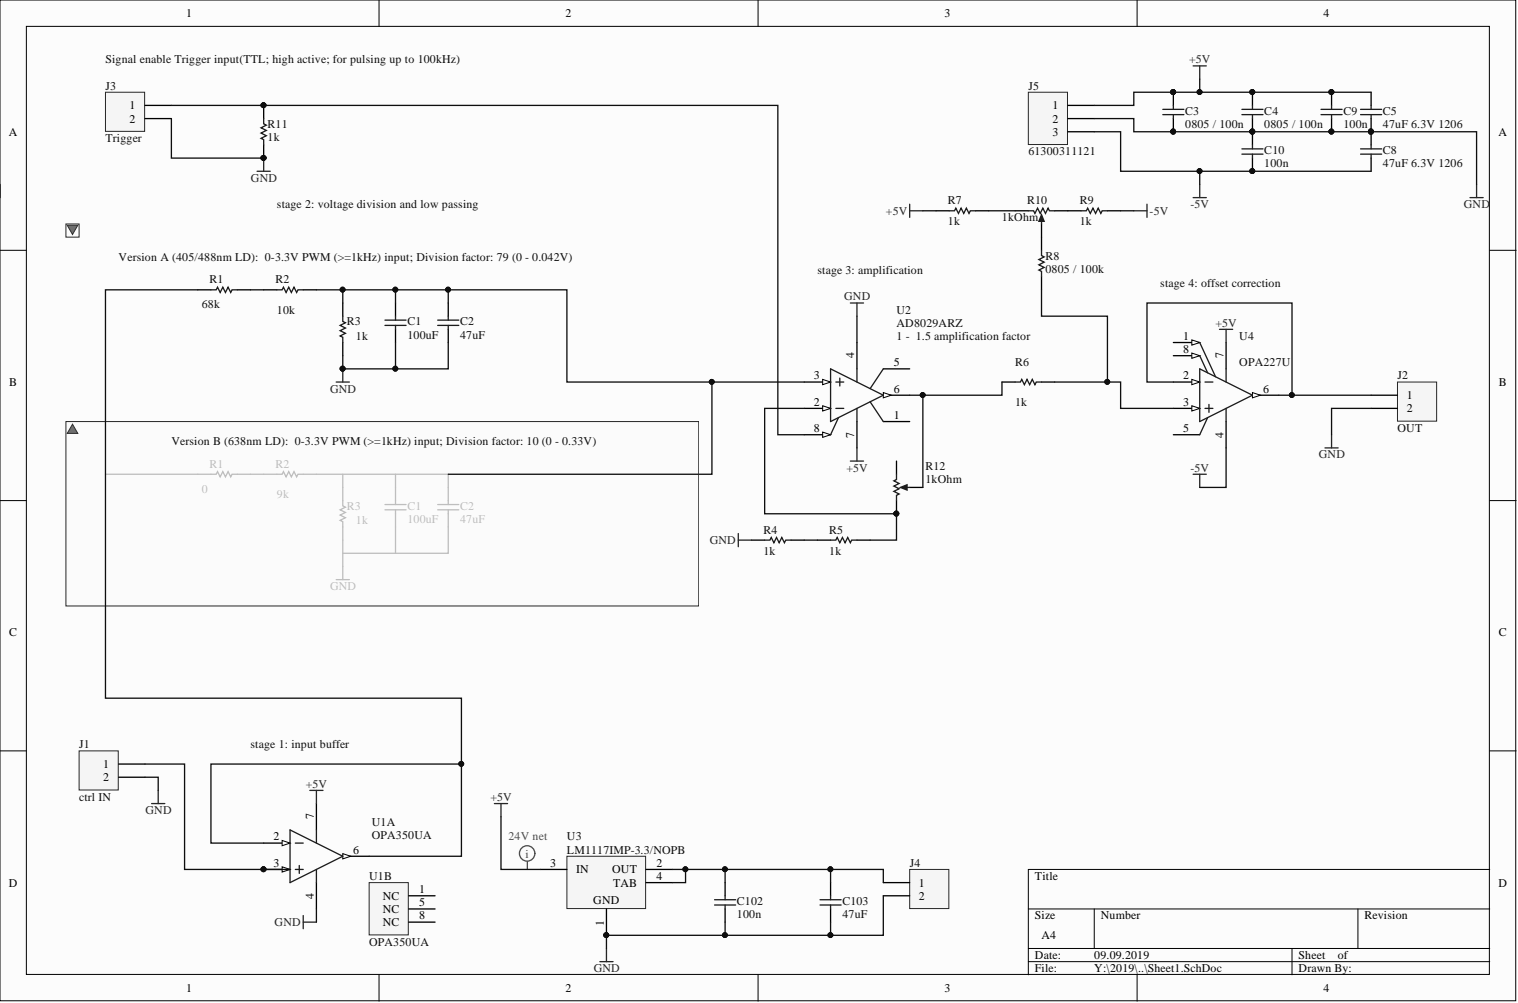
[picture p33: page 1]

Signal enable Trigger input(TTL; high active; for pulsing up to 100kHz)

stage 2: voltage division and low passing

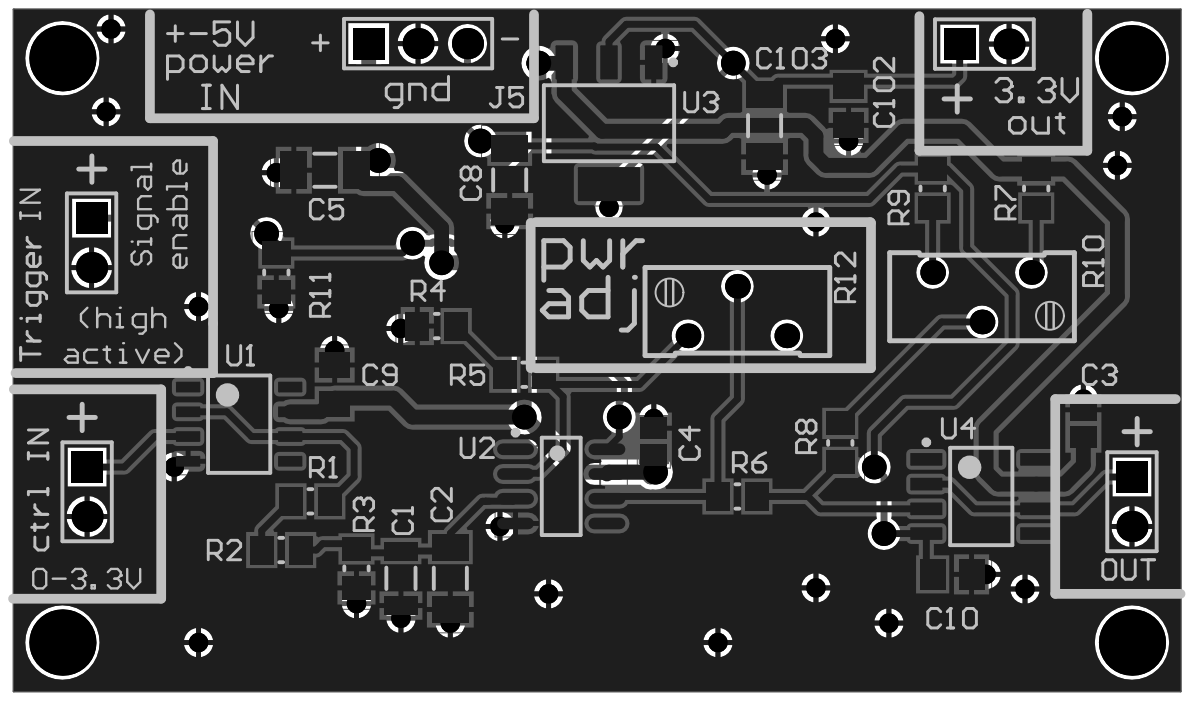
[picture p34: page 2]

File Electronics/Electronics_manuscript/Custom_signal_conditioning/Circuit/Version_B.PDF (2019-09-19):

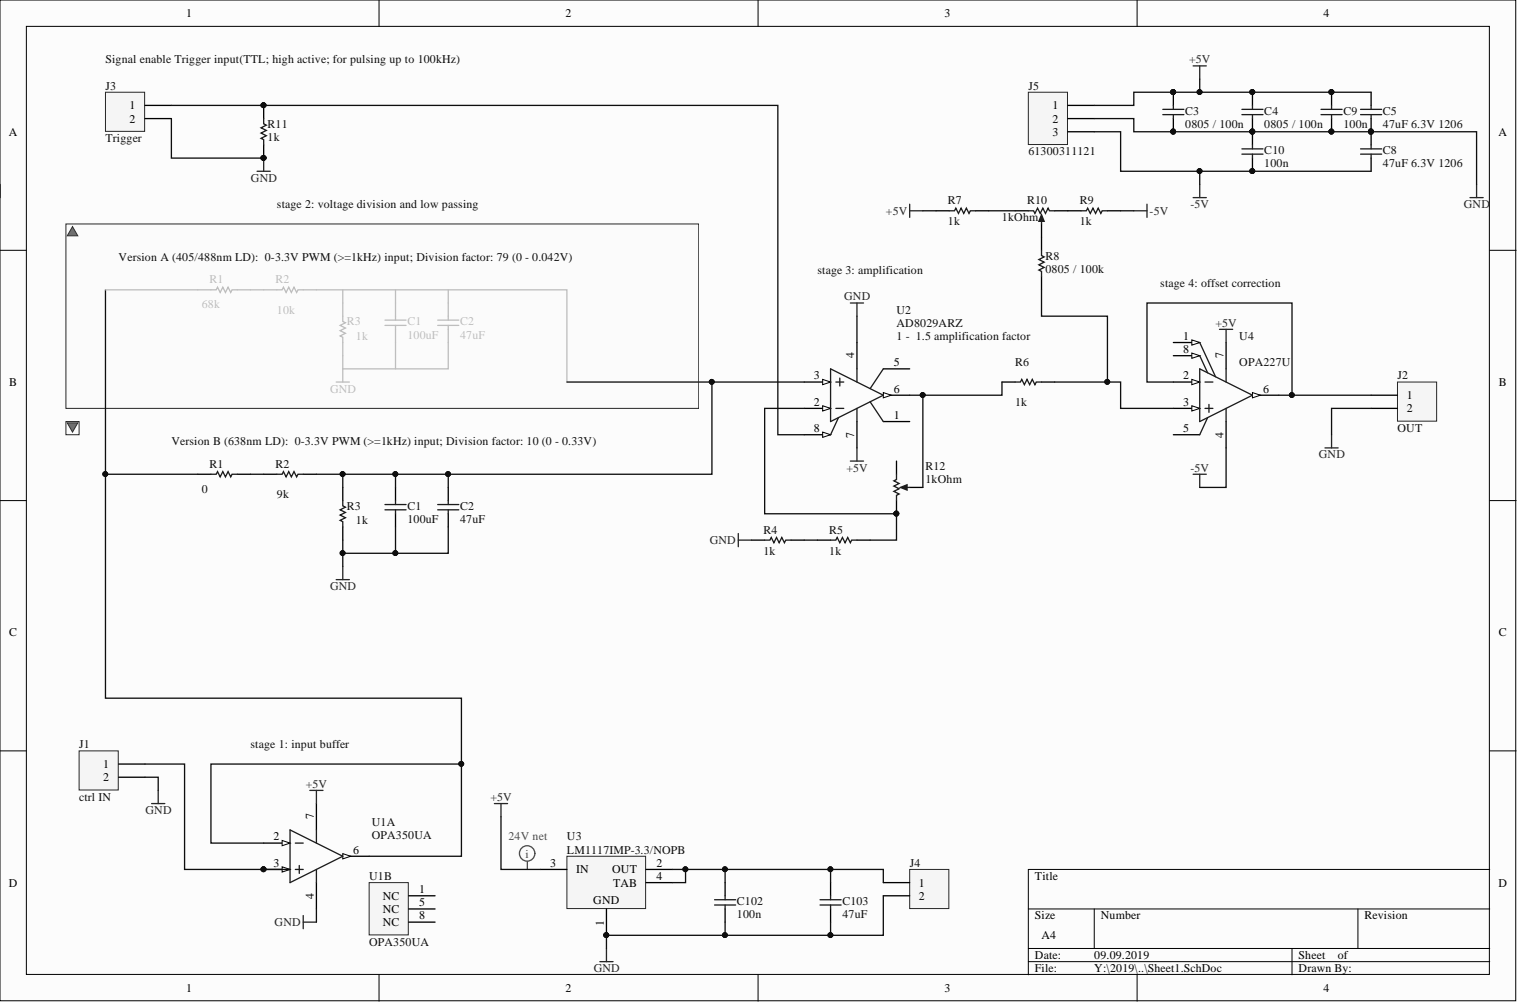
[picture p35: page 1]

Signal enable Trigger input(TTL; high active; for pulsing up to 100kHz)

stage 2: voltage division and low passing

Version A | (405/488nm LD): 0-3.3V PWM (>=1kHz) input; Division factor: 79 (0 - 0.042V) R1 R2

Version B (638nm LD): 0-3.3V PWM (>=1kHz) input; Division factor: 10 (0 - 0.33V)


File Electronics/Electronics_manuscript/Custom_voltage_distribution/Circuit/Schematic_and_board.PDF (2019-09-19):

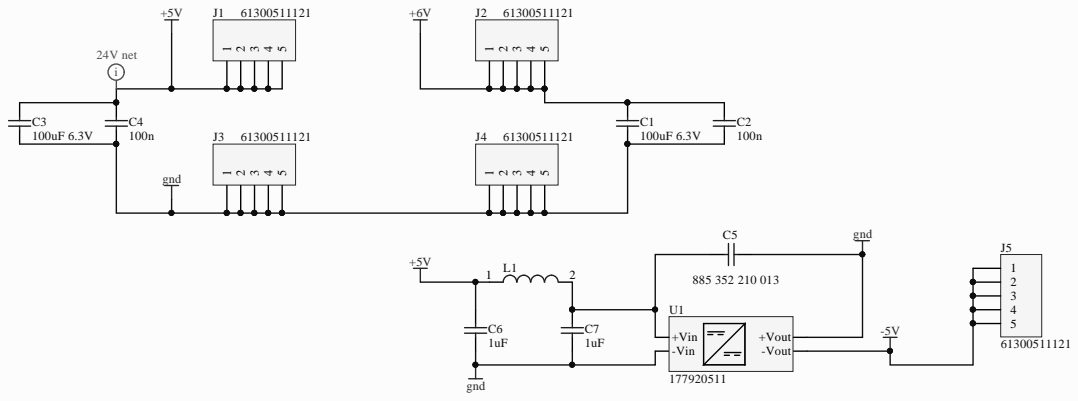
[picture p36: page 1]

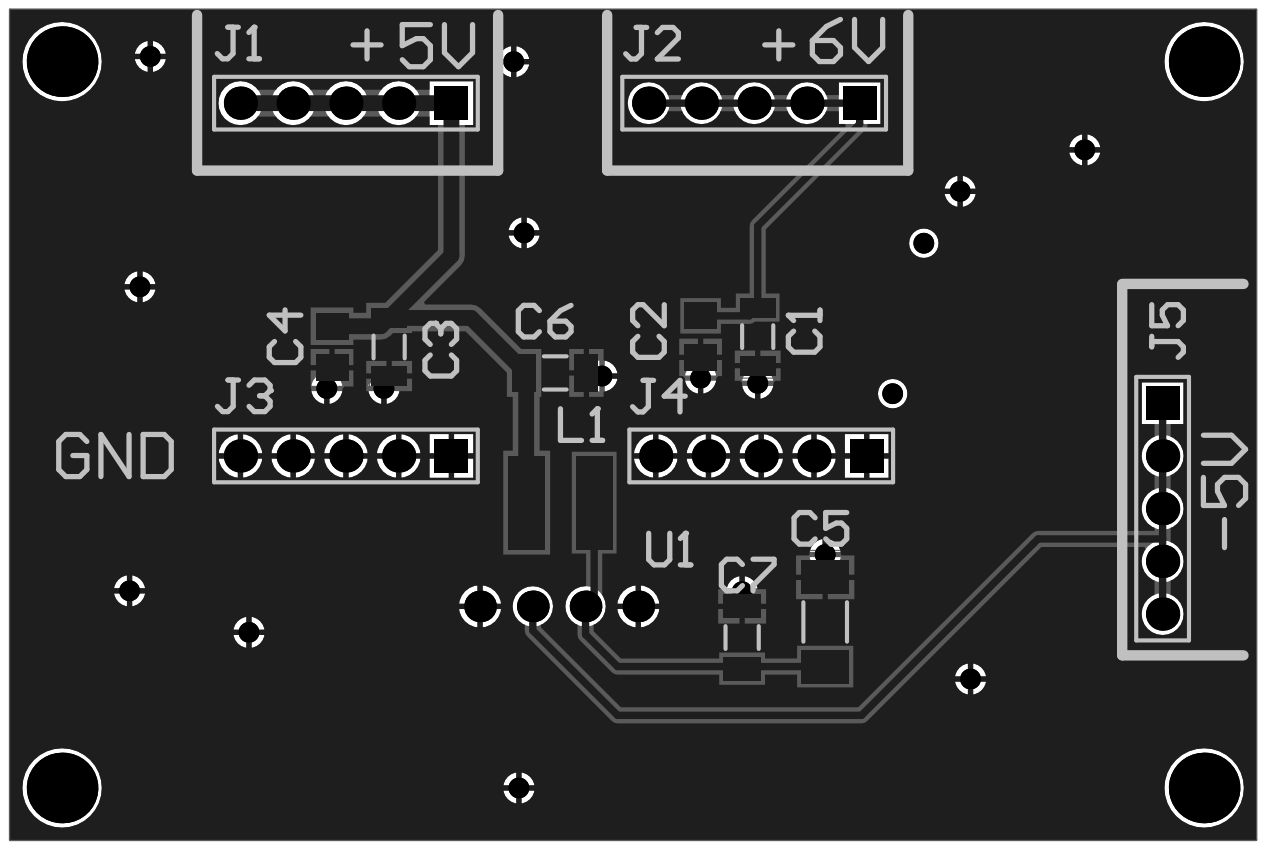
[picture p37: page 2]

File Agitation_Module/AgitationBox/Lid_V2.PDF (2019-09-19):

Aluminium lid

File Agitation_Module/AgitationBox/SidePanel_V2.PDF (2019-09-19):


Aluminium side panel x3

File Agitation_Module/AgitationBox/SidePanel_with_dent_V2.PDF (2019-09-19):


Aluminium side panel with dent

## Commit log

2019-03-12 updated parts list
    [Thorlabs_Cart_WithLSR.xls, Thorlabs_Cart_WithoutLSR.xls, Thorlabs_Comments_on_items.csv]
2019-04-12 added screws to parts list and corrected a typo
    [Thorlabs_Cart_WithLSR.xls, Thorlabs_Cart_WithoutLSR.xls, Thorlabs_Comments_on_items.csv]
2019-04-12 corrected typo
    [Thorlabs_Cart_WithoutLSR.xls, Thorlabs_Comments_on_items.csv]
2019-04-12 another typo
    [Thorlabs_Comments_on_items.csv]
2019-08-09 update with Square fiber
    [Diodes_Driver_Motor.csv, Thorlabs_Cart_WithLSR.xls, Thorlabs_Cart_WithoutLSR.xls, Thorlabs_Comments_on_items.csv]
2019-08-09 updated heat sink part number
    [Diodes_Driver_Motor.csv]
2019-08-09 removed adapter screws (included in 1'' post)
    [Thorlabs_Cart_WithLSR.xls, Thorlabs_Cart_WithoutLSR.xls, Thorlabs_Comments_on_items.csv]
2019-09-19 added private repository
    [AgitationBox_v1_Vibration_Motor.csv, AgitationBox_v2_Brushless_Motor.csv, Agitation_motor_housing_v2.stl, BOM.xlsx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]
2019-09-19 fix some links
    [Diodes.csv]
2019-10-29 added 3mf MotorHousingV2 file
    [Agitation_motor_housing_v2.3mf]
2019-11-20 correction wiring.pdf and note about .stl housing v2 problems
2019-11-27 updated link for motor v2
    [AgitationBox_v2_Brushless_Motor.csv]
2019-11-27 updated motor v2 designs
    [Agitation_motor_housing_v2.3mf, Agitation_motor_housing_v2.stl, Agitation_motor_housing_v2_10mmBearing.STEP, Agitation_motor_housing_v2_10mmBearing.STL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]
2019-11-27 added size reference to motor v2 housing
2019-12-11 changed screw size in motor v2 housing
2020-07-24 added manuscript electronics gerber files
    [board.GBL, board.GBO, board.GBP, board.GBS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]
